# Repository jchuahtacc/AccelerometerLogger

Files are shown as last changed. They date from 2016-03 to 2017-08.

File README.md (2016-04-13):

# Accelerometer Logger

This project is an WiFi enabled accelerometer, built for engineering and physics students to wirelessly capture acceleration data.

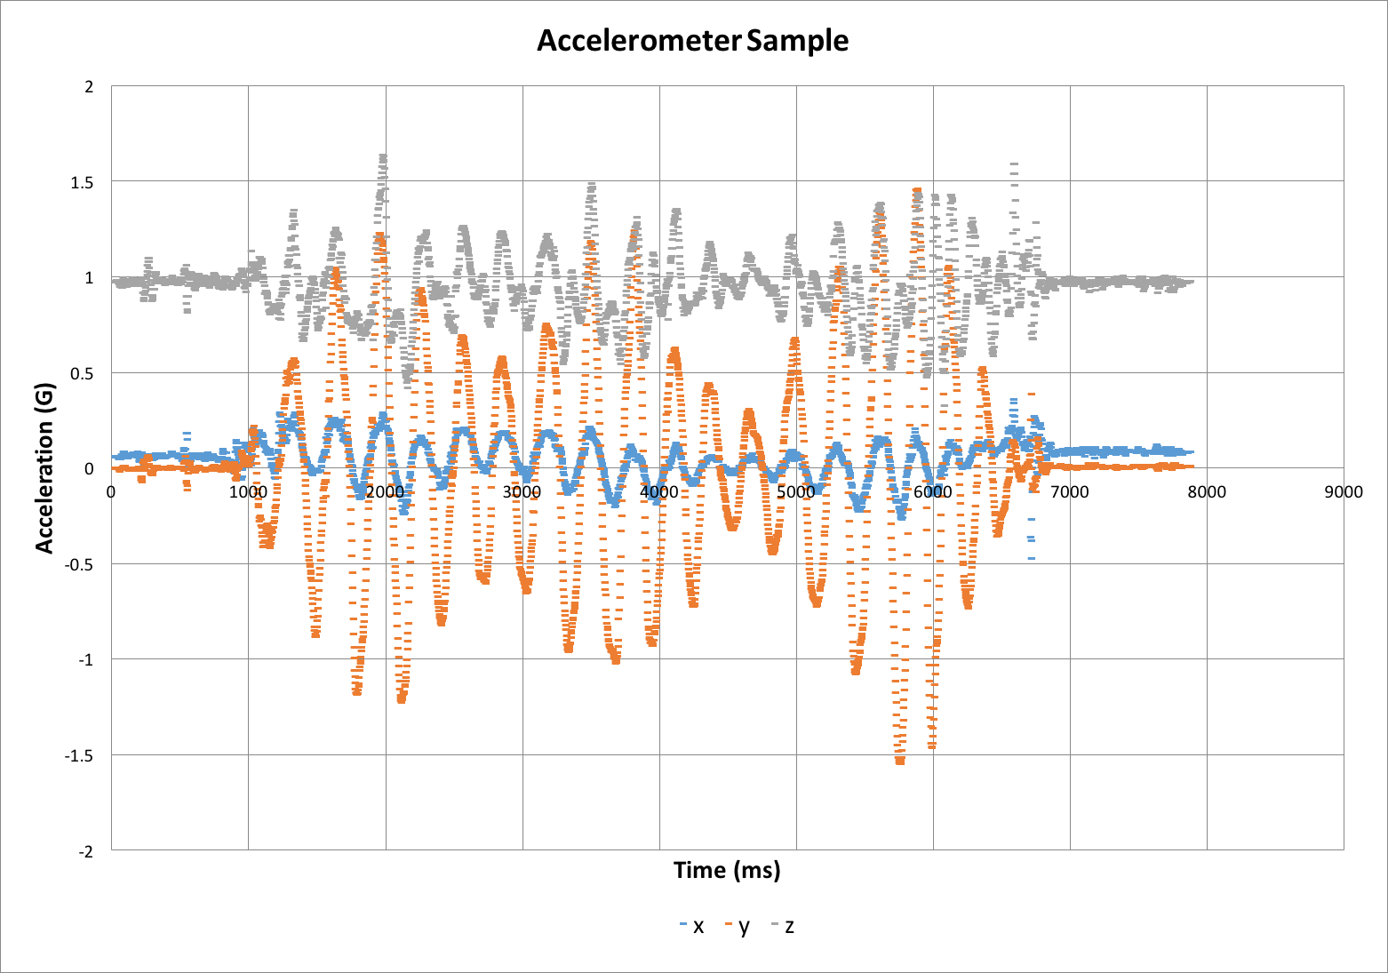
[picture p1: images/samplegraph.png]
Sample Graph


### Introduction

The accelerometer is built using components available on the Internet. At the heart is the LIS3DH accelerometer, capable of ranges up to 16G and sample rates up to 400 Hz. Multiple accelerometers can be used, with simultaneous activation and data collection.

Included in this repository are:

- [Materials list](./MATERIALS.md)
- [Instructions for assembling accelerometers](./ASSEMBLY.md)
- [Firmware source code for the accelerometer](./firmware/)
- [Server source code for capturing data](./server/)
- Sample data and lesson examples

You may download the entire repository [using this link](https://github.com/jchuahtacc/AccelerometerLogger/archive/master.zip).

### Pre-requisite skills

- Some light soldering
- The ability to install some software
- Some light coding and the ability to run a Python script

### License

This software and associated materials are Copyright (c) 2016 by the Texas Advanced Computing Center, protected under the MIT License. [Full text of the license can be found here](./LICENSE.txt).

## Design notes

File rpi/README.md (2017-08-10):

# Setup Instructions for Raspberry Pi Shake Table Controller

### `raspi-config`

```
sudo raspi-config
```

- In `Interfacing Options` enable `SSH`, `SPI` and `I2C`.
- In `Advanced Options` select `Expand Filesystem`
- Reboot

### Installing `jupyter`

```
sudo apt-get install -y python-dev git
sudo pip install --upgrade pip
sudo pip install jupyter
sudo apt-get install -y python-pandas ttf-bistream-vera
```

### Installing the Adafruit Stepper Motor Hat package

```
sudo pip install git+https://github.com/adafruit/Adafruit-Motor-HAT-Python-Library.git
```

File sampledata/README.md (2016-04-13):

# Sample Data

Here is some sample data collected from the Accelerometer.

- [testdata.csv](./testdata.csv): The raw output of the Accelerometer server
- [testdata.xlsx](./testdata.xlsx): An Excel format version with an example graph of the data

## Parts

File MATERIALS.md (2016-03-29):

# Materials

### Basics

- A WiFi router, with WPA2 personal encryption. The device will not connect to an Enterprise network. A home router will suffice - it doesn't need to be connected to the Internet.
- A computer with the following software installed:
 - [Python](https://www.python.org/downloads/)
 - [Arduino IDE](https://www.arduino.cc/en/Main/Software)
 - [ESP8266 USB Drivers](https://www.silabs.com/products/mcu/Pages/USBtoUARTBridgeVCPDrivers.aspx)

### General Supplies

- A soldering iron and solder
- Hook-up wire (22 AWG, solid core)
- Wire cutters and stripper

### Electronic Components

All components are available at Adafruit.com. You can find a [complete wishlist of necessary items](http://www.adafruit.com/wishlists/398580) or search for individual items here:

- [Adafruit Feather Huzzah](https://www.adafruit.com/products/2821)
- [Adafruit FeatherWing Proto](https://www.adafruit.com/products/2884)
- [LIS3DH Accelerometer Breakout](https://www.adafruit.com/products/2809)
- [Feather Header Kit](https://www.adafruit.com/products/2886)
- [500 mAh Lithium Ion Polymer Battery](https://www.adafruit.com/products/1578)

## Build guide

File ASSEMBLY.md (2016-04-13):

# Assembly Instructions

### Introduction

Once you have the materials, you will be constructing two components. One is the Adafruit Feather Huzzah controller and the other is the Featherwing add-on board with the accelerometer. You will need:

- Soldering iron
- Solder
- Wire cutters
- Wire strippers
- 22 AWG hook-up wire

If you have a multi-meter, you can use it to check your work. A video will be posted demonstrating the entire process

### Featherwing Accelerometer Add-On Board

__*Step 1*__

Solder the male header pins onto the Featherwing Proto board. The easiest way to do it is to insert the male header pins into a breadboard to hold them in place, fit the proto board to the top of the male header pins, and then perform your soldering. 

__*Step 2*__

Cut and trim hook-up wire and solder them in place onto the proto board. Here is the wiring diagram:

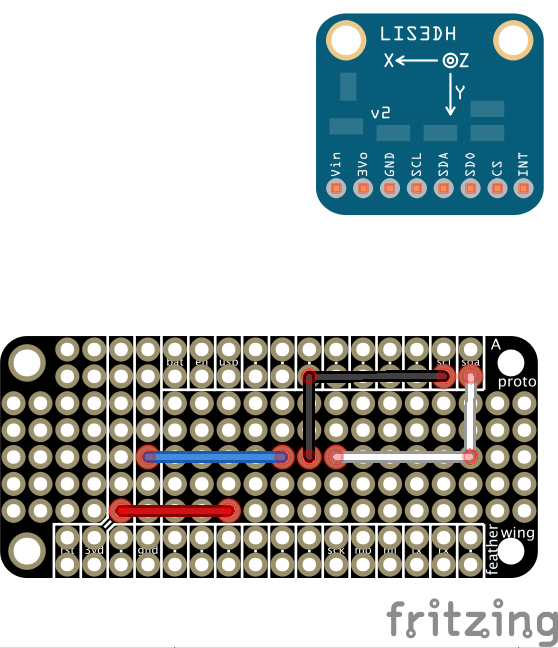
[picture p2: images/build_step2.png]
Step 2


__*Step 3*__

Solder the male header pins onto the accelerometer breakout. Once you have done so, place the breakout on the proto board *above* the wires. Turn the board over and solder it into place. (The placement diagram below appears to show the board below the wires -- this is due to a bug in Fritzing.)

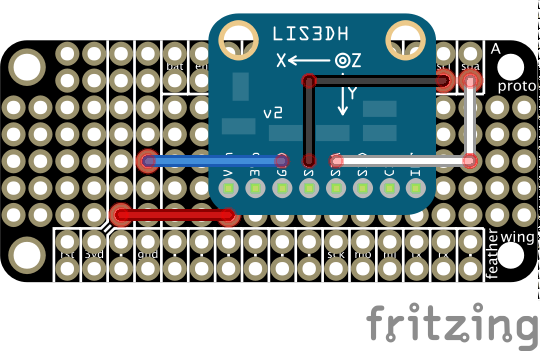
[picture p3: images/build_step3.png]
Step 3


__*Step 4*__

Turn the proto board over. Clip off all of the excess wire and pins in the center of the board from the accelerometer and the hook-up wires. After that, solder a trace from each accelerometer pin to the matching wire next to it.

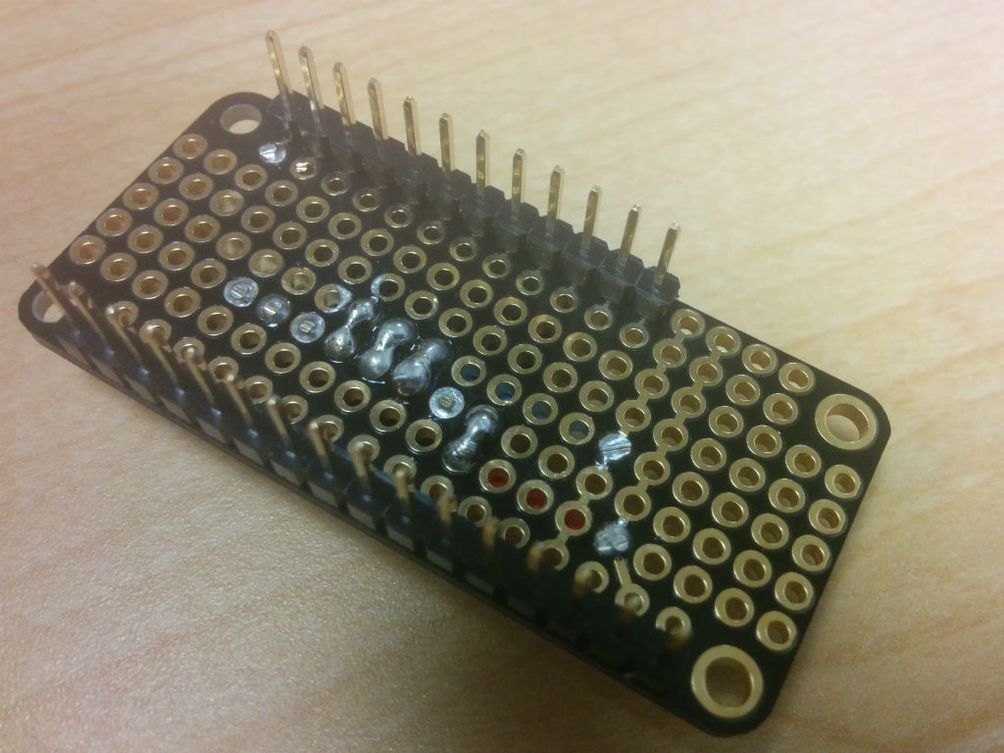
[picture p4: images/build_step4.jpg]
Step 4


### Adafruit Feather Huzzah Assembly

The next component is relatively straightforward to assemble. You must solder the female header onto the Adafruit Feather Huzzah. The easiest way to do that is to place the female headers onto the male header pins on the add-on board, position the Feather Huzzah onto the female headers, and then solder them in place.

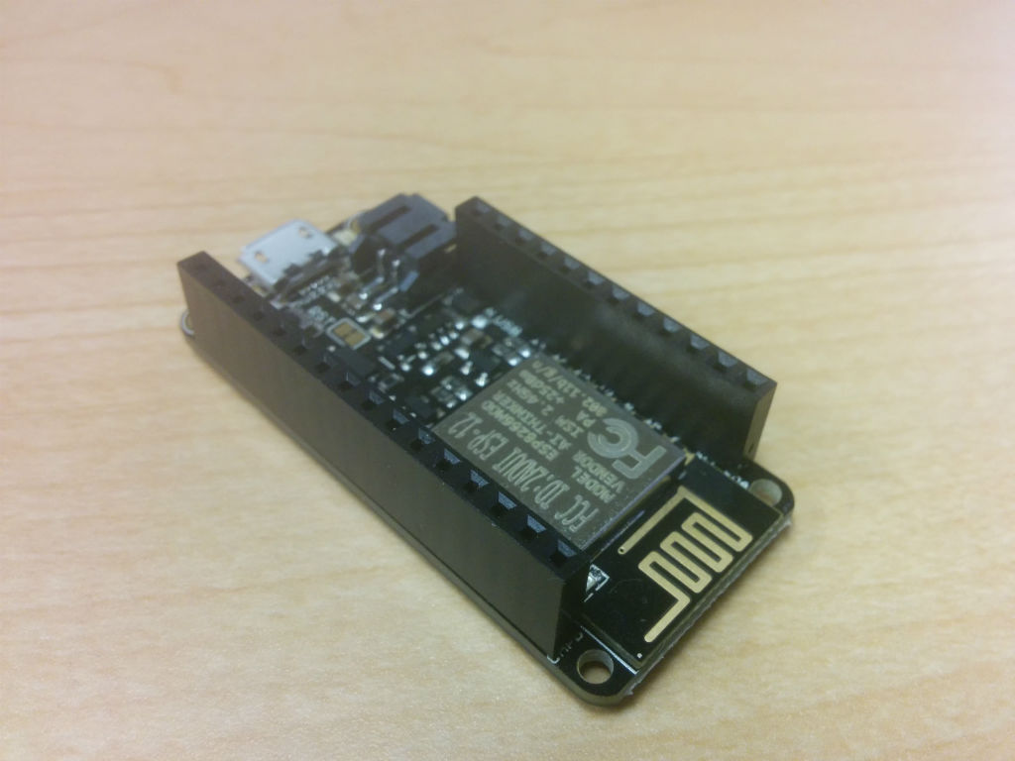
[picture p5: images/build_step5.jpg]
Step 5


### You're finished!

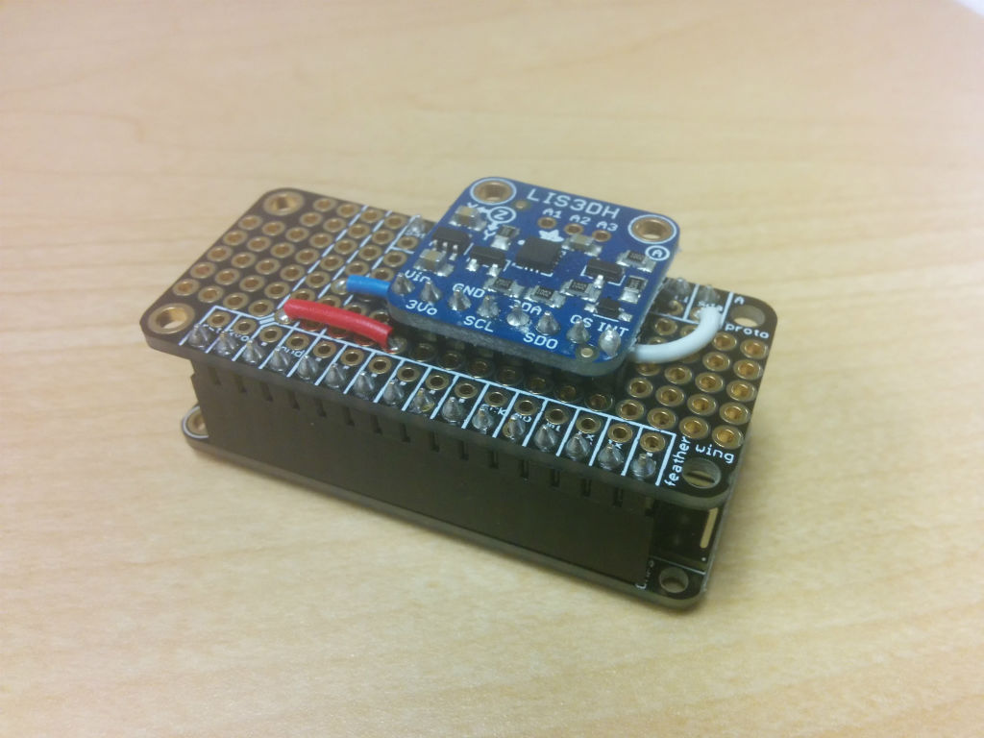
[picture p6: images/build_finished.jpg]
Finished


Some additional notes - If you are attaching a LiPo battery, keep in mind that the battery itself is a little fragile and prone to heating up quickly under usage. Make sure that there is material separating the pin headers on the Accelerometer from the battery itself, to avoid puncturing the battery during use or abuse. A small project box is highly recommended for safety.

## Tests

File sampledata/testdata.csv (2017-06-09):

ip | ms | x | y | z
192.168.1.109 | 2 | 0.05859375 | -0.005859375 | 0.970703125
192.168.1.109 | 4 | 0.056640625 | -0.001953125 | 0.9765625
192.168.1.109 | 7 | 0.05859375 | 0.0 | 0.9765625
192.168.1.109 | 9 | 0.060546875 | -0.00390625 | 0.98046875
192.168.1.109 | 12 | 0.05859375 | -0.005859375 | 0.97265625
192.168.1.109 | 14 | 0.060546875 | -0.001953125 | 0.974609375
192.168.1.109 | 17 | 0.060546875 | -0.001953125 | 0.978515625
192.168.1.109 | 19 | 0.060546875 | 0.0 | 0.98046875
192.168.1.109 | 22 | 0.056640625 | -0.00390625 | 0.98046875
192.168.1.109 | 24 | 0.0546875 | -0.001953125 | 0.97265625
192.168.1.109 | 27 | 0.052734375 | -0.005859375 | 0.9609375
192.168.1.109 | 29 | 0.048828125 | -0.00390625 | 0.966796875
192.168.1.109 | 31 | 0.048828125 | -0.0078125 | 0.96875
192.168.1.109 | 34 | 0.052734375 | -0.013671875 | 0.94921875
192.168.1.109 | 36 | 0.046875 | -0.017578125 | 0.95703125
192.168.1.109 | 40 | 0.052734375 | -0.009765625 | 0.951171875
192.168.1.109 | 43 | 0.046875 | -0.00390625 | 0.966796875
192.168.1.109 | 45 | 0.05078125 | -0.00390625 | 0.951171875
192.168.1.109 | 48 | 0.05859375 | -0.009765625 | 0.943359375
192.168.1.109 | 50 | 0.068359375 | -0.0078125 | 0.955078125
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

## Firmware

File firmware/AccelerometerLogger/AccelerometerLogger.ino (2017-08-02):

// AccelerometerLogger.ino
//
// This firmware for the AccelerometerLogger project is designed to work
// on an ESP8266 microcontroller with an LIS3DH accelerometer.
//
// Configure the variables below to reflect your WiFi SSID and password.
// Also, edit the stationID variable so that your accelerometer can listen
// for server announcements

#define TIMEOUT   11000
#define KEEPALIVE_TIMEOUT 2000

#include "utility/Adafruit_LIS3DH.h"
#include <Adafruit_Sensor.h>
#include <ESP8266WiFi.h>
#include "StatusLED.h"
#include "WifiWrapper.h"

// Change these variables to reflect your configuration
const char* ssid = "codetacc";              // your WiFi access point
const char* password = "codetacc";          // your WiFi password
const char* stationId = "codetacc";         // your accelerometer station ID
const char* clientId = "delta";              // this Accelerometer's client ID

#define STATUS_LED 0

Adafruit_LIS3DH accel = Adafruit_LIS3DH();
StatusLED led = StatusLED(STATUS_LED);
WifiWrapper wifi = WifiWrapper(STATUS_LED, stationId, clientId);

// Method prototypes
void commandError(void);
void configError(void);
void configureAccelerometer(void);
void startStreaming(void);
void haltStreaming(void);
void flashPing(void);
void receiveAnnounce(void);
void timeOut(void);

int eventCount = 0;
int flushCount = 0;
long startTime = 0;
bool sending = false;

long lastKeepAlive = 0;
long lastCommand = 0;

void setup() {
  pinMode(STATUS_LED, OUTPUT);


  Serial.begin(115200);
  if (!accel.begin(0x18)) {
    led.blockingError("Couldn't find accelerometer");
  }
  Serial.println("Accelerometer OK");
  accel.setRange(LIS3DH_RANGE_16_G);
  digitalWrite(STATUS_LED, LOW);
}

void loop() {
  if (!wifi.wifiConnected()) {
    Serial.println("Wifi disconnected");
    led.pulse(3);
    delay(800);
    yield();
    wifi.wifiConnect(ssid, password);
  } else {
    int command = wifi.parseCommand();
    switch (command) {
      case COMMAND_CONFIG_ERROR : configError(); break;
      case COMMAND_UNKNOWN : commandError(); break;
      case COMMAND_CONFIGURE : configureAccelerometer(); break;
      case COMMAND_START : startStreaming(); break;
      case COMMAND_HALT : haltStreaming(); break;
      case COMMAND_PING : flashPing(); break;
      case COMMAND_ANNOUNCE : receiveAnnounce(); break;
    }
    if (sending) {
      if (accel.dataReady()) {
        accel.read();
        led.off();
        if (!wifi.send(millis() - startTime, accel.x, accel.y, accel.z)) {
          Serial.println("Couldn't send data to the server");
          led.pulse(5);
        }
        delay(1);
        led.on();
      }
    } else if (command == COMMAND_NONE) {
      if (millis() - lastCommand > TIMEOUT) {
        timeOut();
        led.on();
        delay(500);
        yield();
        led.off();
        delay(500);
      }
    } else {
      led.on();
      lastCommand = millis();
    }
    if (millis() - lastKeepAlive > KEEPALIVE_TIMEOUT) {
      wifi.sendClientId();
      lastKeepAlive = millis();
    }
  }
}

void flashPing() {
  Serial.println("Received ping");
  led.flash(2);
  delay(500);
  led.flash(2);
  delay(500);
  led.flash(2);
}

void startStreaming() {
  Serial.println("Starting data streaming");
  led.flash(3);
  sending = true;
  startTime = millis();
}

void haltStreaming() {
  Serial.println("Halting data streaming");
  sending = false;
  wifi.flush();
  led.flash(3);
}

void commandError() {
  Serial.println("Got a bad command from the server");
}

void configError() {
  Serial.println("Got a bad configuration parameter from the server");
}

void receiveAnnounce() {
  Serial.println("Received server announcement");
  wifi.sendClientId();
}

void timeOut() {
  Serial.println("Server timed out");
  wifi.dropServer();
}

void configureAccelerometer() {
  Serial.println("Accelerometer configuration requested");
  switch (wifi.requestedRate) {
    case CONFIG_1HZ : Serial.println("Rate 1Hz"); accel.setDataRate(LIS3DH_DATARATE_1_HZ); break;
    case CONFIG_10HZ : Serial.println("Rate 10Hz"); accel.setDataRate(LIS3DH_DATARATE_10_HZ); break;
    case CONFIG_25HZ : Serial.println("Rate 25Hz"); accel.setDataRate(LIS3DH_DATARATE_25_HZ); break;
    case CONFIG_50HZ : Serial.println("Rate 50Hz"); accel.setDataRate(LIS3DH_DATARATE_50_HZ); break;
    case CONFIG_100HZ : Serial.println("Rate 100Hz"); accel.setDataRate(LIS3DH_DATARATE_100_HZ); break;
    case CONFIG_200HZ : Serial.println("Rate 200Hz"); accel.setDataRate(LIS3DH_DATARATE_200_HZ); break;
    case CONFIG_400HZ : Serial.println("Rate 400Hz"); accel.setDataRate(LIS3DH_DATARATE_400_HZ); break;
    default : configError(); break;
  }
  switch (wifi.requestedRange) {
    case CONFIG_2G : Serial.println("Range 2G"); accel.setRange(LIS3DH_RANGE_2_G); break;
    case CONFIG_4G : Serial.println("Range 4G"); accel.setRange(LIS3DH_RANGE_4_G); break;
    case CONFIG_8G : Serial.println("Range 8G"); accel.setRange(LIS3DH_RANGE_8_G); break;
    case CONFIG_16G : Serial.println("Range 16G"); accel.setRange(LIS3DH_RANGE_16_G); break;
    default : configError(); break;
  }
  led.flash(3);
}

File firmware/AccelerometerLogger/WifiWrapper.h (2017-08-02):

#include <ESP8266WiFi.h>
#include <WiFiUdp.h>
#include "StatusLED.h"

#define MAX_TIMEOUT 30
#define PORT 9999

#define COMMAND_CONFIG_ERROR          -3
#define COMMAND_UNKNOWN               -2
#define COMMAND_DISCONNECTED          -1
#define COMMAND_NONE                  0
#define COMMAND_CONFIGURE             1
#define COMMAND_START                 2
#define COMMAND_HALT                  3
#define COMMAND_KEEPALIVE             4
#define COMMAND_PING                  5
#define COMMAND_ANNOUNCE              6

#define OPCODE_CONFIGURE              'r'
#define OPCODE_START                  's'
#define OPCODE_HALT                   'h'
#define OPCODE_KEEPALIVE              'k'     // unused on server side, for now
#define OPCODE_PING                   'p'
#define OPCODE_ANNOUNCE               'a'
#define RESPONSECODE_DATA             'd'
#define RESPONSECODE_CLIENT           'c'

#define CONFIG_1HZ                    'a'
#define CONFIG_10HZ                   'b'
#define CONFIG_25HZ                   'c'
#define CONFIG_50HZ                   'd'
#define CONFIG_100HZ                  'e'
#define CONFIG_200HZ                  'f'
#define CONFIG_400HZ                  'g'

#define CONFIG_2G                     'a'
#define CONFIG_4G                     'b'
#define CONFIG_8G                     'c'
#define CONFIG_16G                    'd'

#define SEND_BUFFER_LENGTH            1024
#define SEND_BUFFER_WATERMARK         990

class WifiWrapper {
public:
  WifiWrapper(int, const char*, const char*);
  bool wifiConnect(const char*, const char *);
  bool wifiConnected(void);
  bool serverConnected(void);
  bool send(long, int, int, int);
  void sendClientId();
  void flush(void);
  void dropServer(void);
  int parseCommand(void);
  char requestedRate;
  char requestedRange;
protected:

private:
  bool udp_send(char, const char*);
  WiFiUDP udp;
  IPAddress serverIp;
  IPAddress blankIp;
  StatusLED led = NULL;
  char response_buffer[10];
  char send_buffer[SEND_BUFFER_LENGTH] = { 0 };
  const char* station_id;
  const char* client_id;
  int bufferPosition = 0;
  int writesSinceFlush = 0;
};

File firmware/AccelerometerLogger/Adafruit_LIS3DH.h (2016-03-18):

/**************************************************************************/
/*!
    @file     Adafruit_LIS3DH.h
    @author   K. Townsend / Limor Fried (Adafruit Industries)
    @license  BSD (see license.txt)

    This is a library for the Adafruit LIS3DH Accel breakout board
    ----> https://www.adafruit.com/products/2809

    Adafruit invests time and resources providing this open source code,
    please support Adafruit and open-source hardware by purchasing
    products from Adafruit!

    @section  HISTORY

    v1.0  - First release
*/
/**************************************************************************/

#if ARDUINO >= 100
 #include "Arduino.h"
#else
 #include "WProgram.h"
#endif

#include <Wire.h>
#ifndef __AVR_ATtiny85__
  #include <SPI.h>
#endif
#include <Adafruit_Sensor.h>

/*=========================================================================
    I2C ADDRESS/BITS
    -----------------------------------------------------------------------*/
    #define LIS3DH_DEFAULT_ADDRESS  (0x18)    // if SDO/SA0 is 3V, its 0x19
/*=========================================================================*/

#define LIS3DH_REG_STATUS1       0x07
#define LIS3DH_REG_OUTADC1_L     0x08
#define LIS3DH_REG_OUTADC1_H     0x09
#define LIS3DH_REG_OUTADC2_L     0x0A
#define LIS3DH_REG_OUTADC2_H     0x0B
#define LIS3DH_REG_OUTADC3_L     0x0C
#define LIS3DH_REG_OUTADC3_H     0x0D
#define LIS3DH_REG_INTCOUNT      0x0E
#define LIS3DH_REG_WHOAMI        0x0F
#define LIS3DH_REG_TEMPCFG       0x1F
#define LIS3DH_REG_CTRL1         0x20
#define LIS3DH_REG_CTRL2         0x21
#define LIS3DH_REG_CTRL3         0x22
#define LIS3DH_REG_CTRL4         0x23
#define LIS3DH_REG_CTRL5         0x24
#define LIS3DH_REG_CTRL6         0x25
#define LIS3DH_REG_REFERENCE     0x26
#define LIS3DH_REG_STATUS2       0x27
#define LIS3DH_REG_OUT_X_L       0x28
#define LIS3DH_REG_OUT_X_H       0x29
#define LIS3DH_REG_OUT_Y_L       0x2A
#define LIS3DH_REG_OUT_Y_H       0x2B
#define LIS3DH_REG_OUT_Z_L       0x2C
#define LIS3DH_REG_OUT_Z_H       0x2D
#define LIS3DH_REG_FIFOCTRL      0x2E
#define LIS3DH_REG_FIFOSRC       0x2F
#define LIS3DH_REG_INT1CFG       0x30
#define LIS3DH_REG_INT1SRC       0x31
#define LIS3DH_REG_INT1THS       0x32
#define LIS3DH_REG_INT1DUR       0x33
#define LIS3DH_REG_CLICKCFG      0x38
#define LIS3DH_REG_CLICKSRC      0x39
#define LIS3DH_REG_CLICKTHS      0x3A
#define LIS3DH_REG_TIMELIMIT     0x3B
#define LIS3DH_REG_TIMELATENCY   0x3C
#define LIS3DH_REG_TIMEWINDOW    0x3D

typedef enum
{
  LIS3DH_RANGE_16_G         = 0b11,   // +/- 16g
  LIS3DH_RANGE_8_G           = 0b10,   // +/- 8g
  LIS3DH_RANGE_4_G           = 0b01,   // +/- 4g
  LIS3DH_RANGE_2_G           = 0b00    // +/- 2g (default value)
} lis3dh_range_t;

typedef enum
{
  LIS3DH_AXIS_X         = 0x0,
  LIS3DH_AXIS_Y         = 0x1,
  LIS3DH_AXIS_Z         = 0x2,
} lis3dh_axis_t;


/* Used with register 0x2A (LIS3DH_REG_CTRL_REG1) to set bandwidth */
typedef enum
{
  LIS3DH_DATARATE_400_HZ     = 0b0111, //  400Hz
  LIS3DH_DATARATE_200_HZ     = 0b0110, //  200Hz
  LIS3DH_DATARATE_100_HZ     = 0b0101, //  100Hz
  LIS3DH_DATARATE_50_HZ      = 0b0100, //   50Hz
  LIS3DH_DATARATE_25_HZ      = 0b0011, //   25Hz
  LIS3DH_DATARATE_10_HZ      = 0b0010, // 10 Hz
  LIS3DH_DATARATE_1_HZ       = 0b0001, // 1 Hz
  LIS3DH_DATARATE_POWERDOWN  = 0,
  LIS3DH_DATARATE_LOWPOWER_1K6HZ  = 0b1000,
  LIS3DH_DATARATE_LOWPOWER_5KHZ  =  0b1001,

} lis3dh_dataRate_t;

class Adafruit_LIS3DH : public Adafruit_Sensor {
 public:
  Adafruit_LIS3DH(void);
  Adafruit_LIS3DH(int8_t cspin);
  Adafruit_LIS3DH(int8_t cspin, int8_t mosipin, int8_t misopin, int8_t sckpin);

  bool       begin(uint8_t addr = LIS3DH_DEFAULT_ADDRESS);

  void read();
  int16_t readADC(uint8_t a);

  void setRange(lis3dh_range_t range);
  lis3dh_range_t getRange(void);

  void setDataRate(lis3dh_dataRate_t dataRate);
  lis3dh_dataRate_t getDataRate(void);

  bool dataReady(void);
  void setFifoMode(void);

  bool getEvent(sensors_event_t *event);
  void getSensor(sensor_t *sensor);

  uint8_t getOrientation(void);

  void setClick(uint8_t c, uint8_t clickthresh, uint8_t timelimit = 10, uint8_t timelatency = 20, uint8_t timewindow = 255);
  uint8_t getClick(void);

  int16_t x, y, z;
  float x_g, y_g, z_g;

 private:

  uint8_t readRegister8(uint8_t reg);
  void writeRegister8(uint8_t reg, uint8_t value);
  uint8_t spixfer(uint8_t x = 0xFF);
  uint16_t divider = 2048;

  int32_t _sensorID;
  int8_t  _i2caddr;

  // SPI
  int8_t _cs, _mosi, _miso, _sck;
};

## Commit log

2016-03-07 SDLogger init and error LED blink codes.
2016-03-17 Eliminating SD card, moving to wifi reporting to python server socket
2016-03-17 Got threading working
2016-03-19 Transferred data streaming functions to UDP service
    [shake.csv, udpdata.csv, udpdata2.csv]
2016-03-19 Server now divides raw integer results into correct range readings
    [shake.csv, testdata.csv, testdata.xlsx, udpdata.csv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]
2016-03-19 Implemented print status
2016-03-22 Cleaned up directories
    [testdata.csv, testdata.xlsx]
2016-03-29 Documentation started
    [testdata.xlsx]
2016-03-29 Started frizzing
    [logger.fzz]
2016-03-30 More documentation
    [logger.fzz]
2017-06-08 Added ability to signal sensor for identification
2017-06-09 Added column headers
    [testdata.csv]
2017-08-10 Raspberry Pi setup insructions
